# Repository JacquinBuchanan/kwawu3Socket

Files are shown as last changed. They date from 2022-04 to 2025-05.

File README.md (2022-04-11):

# Kwawu Arm 3.0 - Socket Version

This is a 3D Printable functional device for those with forearm limb differences. It has better functionality and easier to assemble than the Kwawu 2.0 version.

!!!! DO NOT PRINT THESE STL FILES DIRECTLY. !!!!!
Download all the files and use the OpenSCAD to modify and scale the STL files.

The included PDF file "Kwawu 3.0 Socket Version Instructional Guide" will show you how to download the Open SCAD program and use the code in these files to size this model.

Instructional videos for this design can be found here.
https://www.youtube.com/playlist?list=PLO2iVws0boe0Yrh_1auXd5TTmXr6_y3zT

I have redesigned the Kwawu arm to be more natural looking and more functional. The terminal device has a much higher grip strength and functionality. Very good at picking up small things with index finger and thumb and big things with whole hand.

This version is the socket version intended for people with short forearm residual limbs.
There is a wrap version for people with long forearm residuals

I would like to thank the e-NABLE community. It is a wonderful group to be a part of.

To get involved with the e-NABLE community please visit https://hub.e-nable.org

Shield: [][cc-by]

This work is licensed under a
[Creative Commons Attribution 4.0 International License][cc-by].

[][cc-by]

[cc-by]: http://creativecommons.org/licenses/by/4.0/
[cc-by-image]: https://i.creativecommons.org/l/by/4.0/88x31.png
[cc-by-shield]: https://img.shields.io/badge/License-CC%20BY%204.0-lightgrey.svg

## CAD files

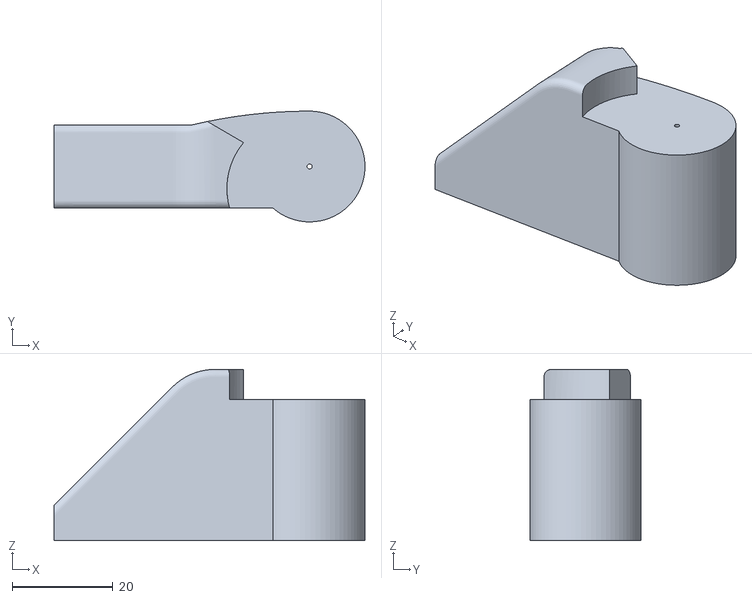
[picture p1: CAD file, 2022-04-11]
o_Arm2.stl
61.7 x 22.0 x 34.0

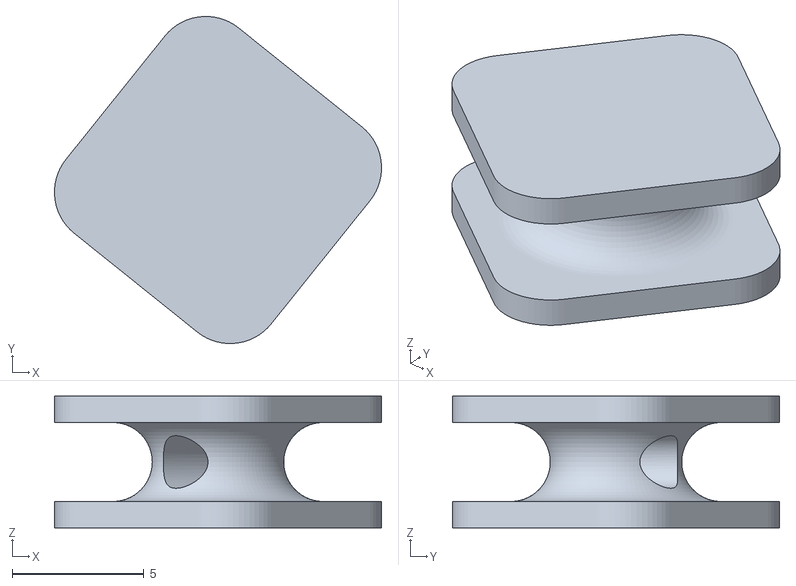
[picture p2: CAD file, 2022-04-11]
o_Tensioner.stl
12.4 x 12.4 x 5.00

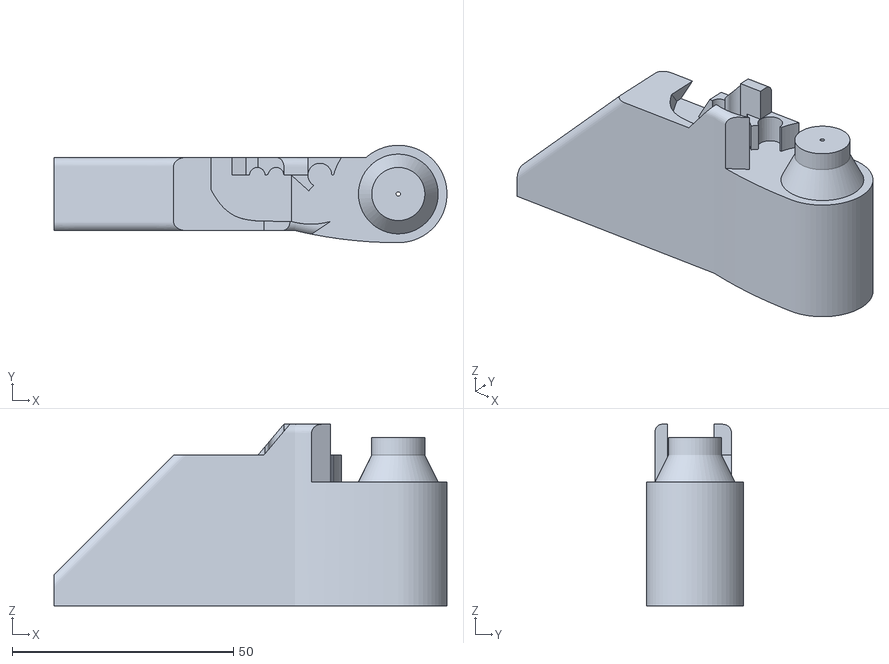
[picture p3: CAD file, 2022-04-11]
o_Arm1.stl
88.7 x 22.0 x 41.0

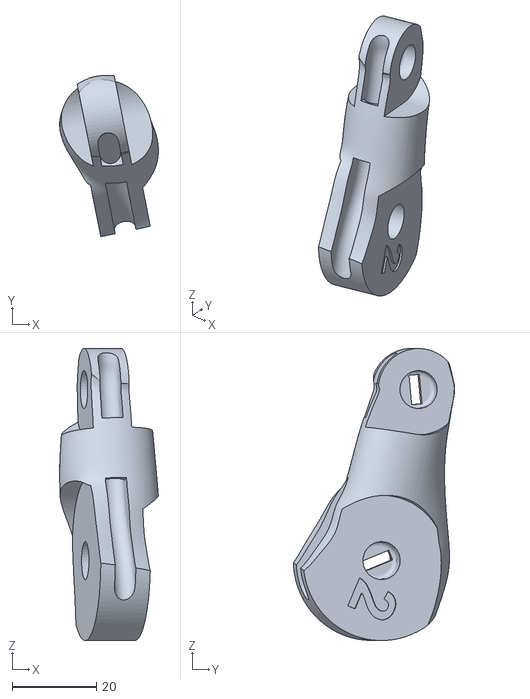
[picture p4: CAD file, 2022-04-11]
o_IndexFingerPhalanx.stl
23.4 x 38.3 x 69.3

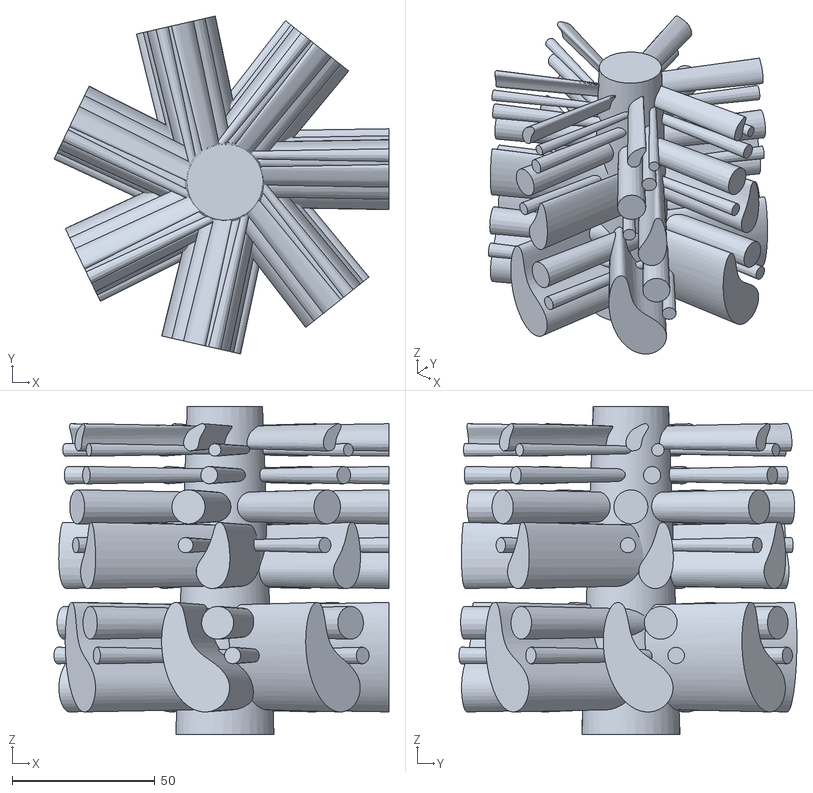
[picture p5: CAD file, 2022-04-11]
o_VentHoles11.stl
117.4 x 118.4 x 115.0

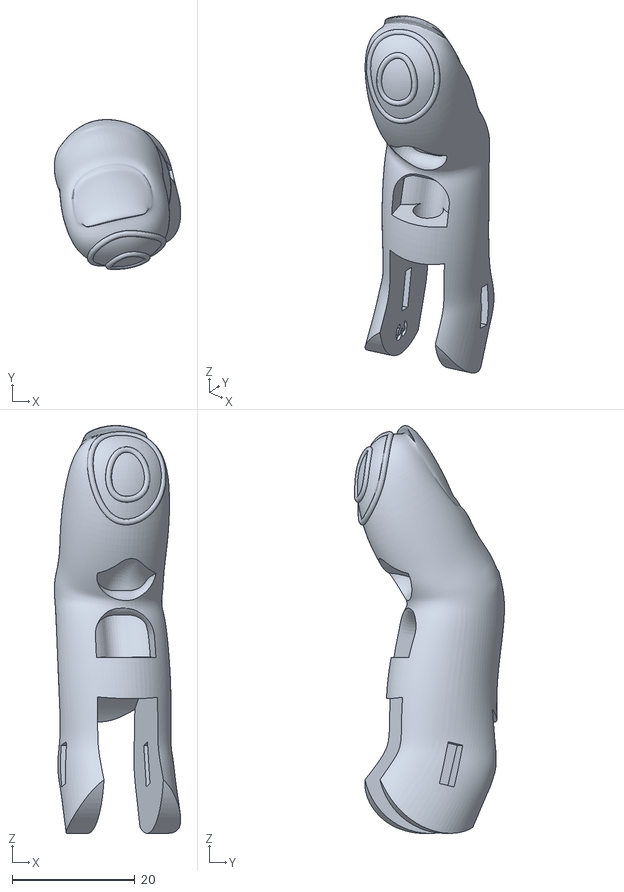
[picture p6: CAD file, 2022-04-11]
o_MiddleFingerEnd.stl
20.6 x 24.5 x 66.6

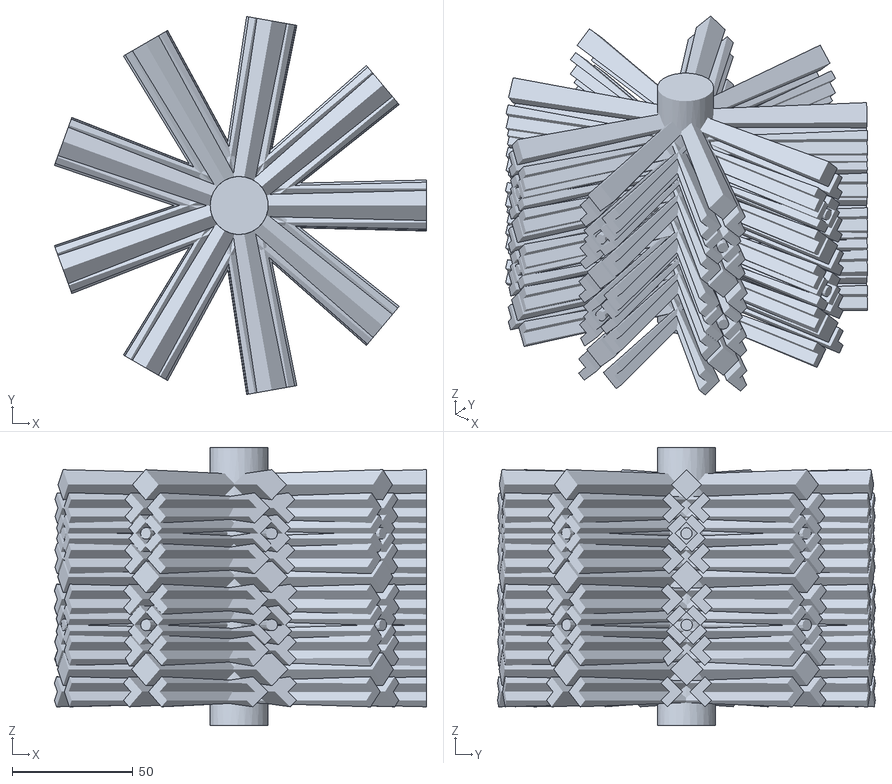
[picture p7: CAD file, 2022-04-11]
o_VentHoles31.stl
153.9 x 156.3 x 115.0

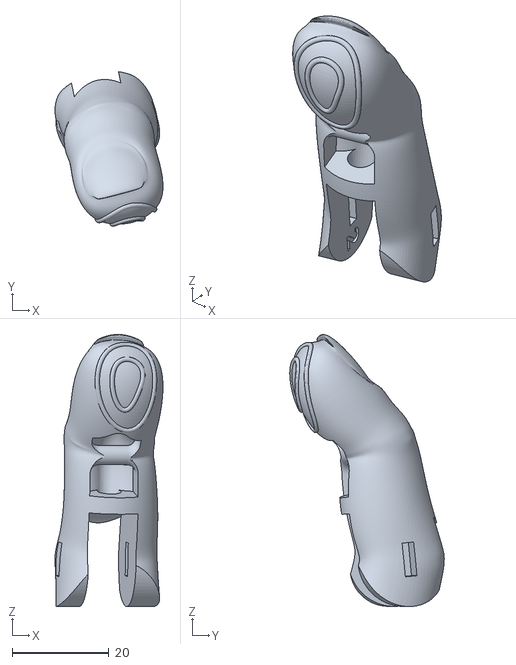
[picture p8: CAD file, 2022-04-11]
o_IndexFingerEnd.stl
22.3 x 31.9 x 56.2

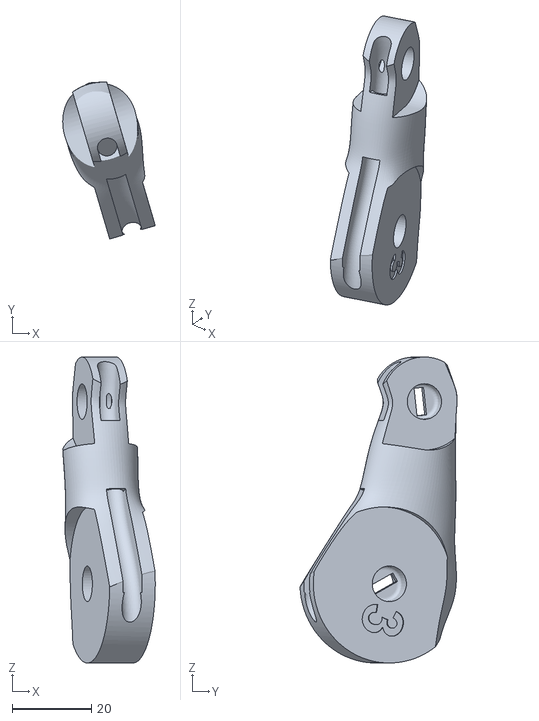
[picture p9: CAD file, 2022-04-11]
o_MiddleFingerPhalanx.stl
23.4 x 39.6 x 77.3

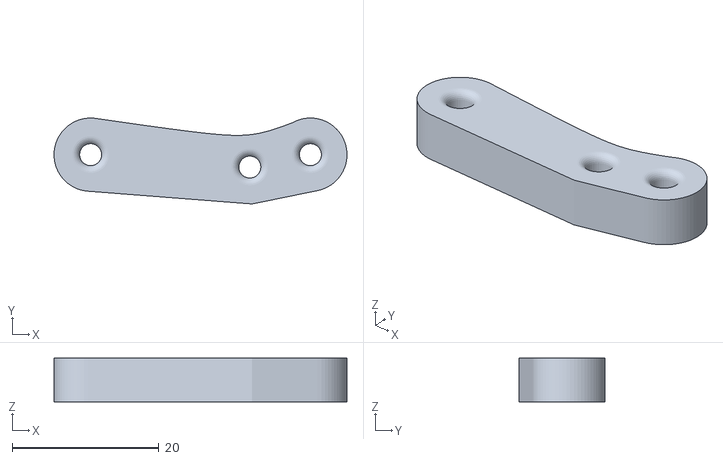
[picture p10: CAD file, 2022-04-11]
o_WhippleTreeSecondary.stl
40.0 x 11.7 x 6.00

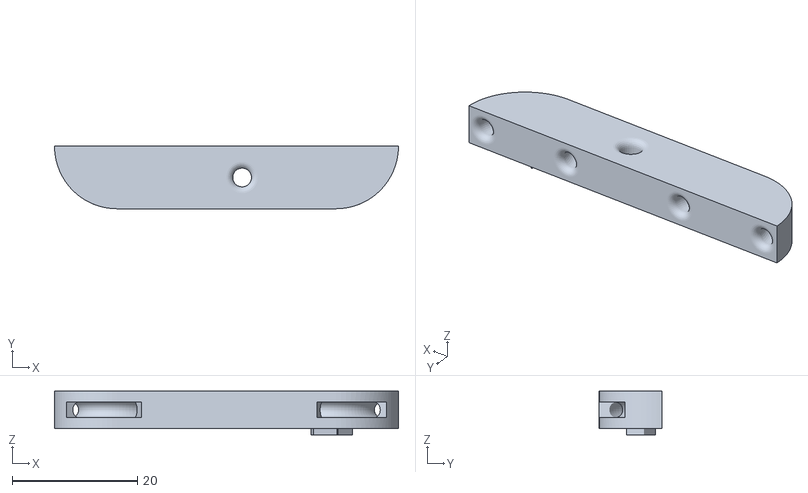
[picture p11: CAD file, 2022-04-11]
o_WhippleTreePrimary.stl
55.0 x 10.0 x 7.00

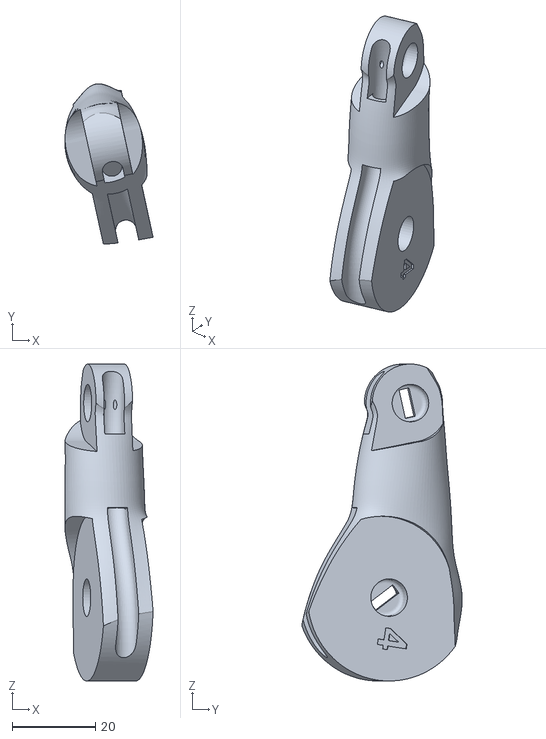
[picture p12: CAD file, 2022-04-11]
o_RingFingerPhalanx.stl
21.1 x 38.5 x 76.1

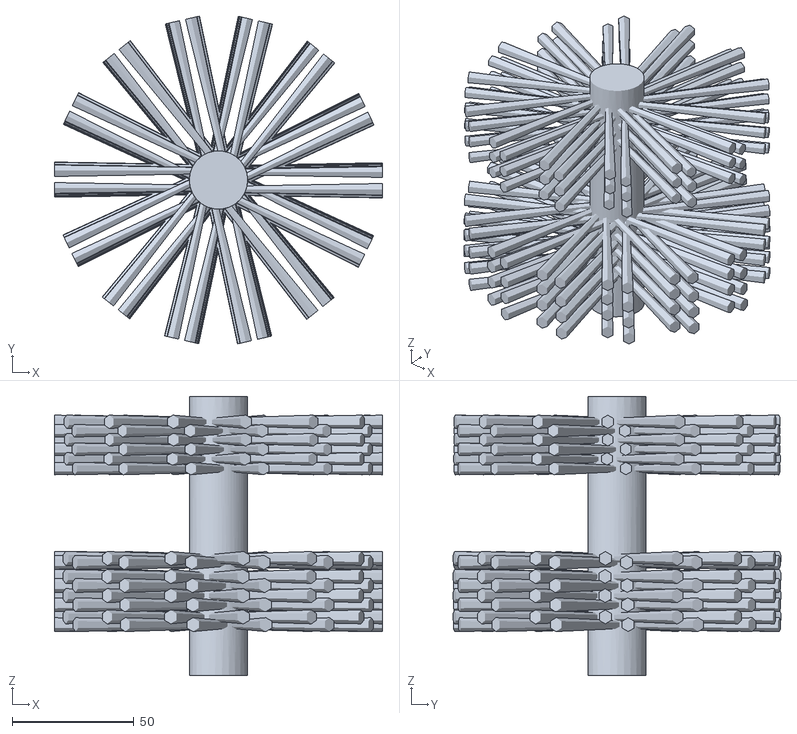
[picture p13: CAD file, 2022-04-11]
o_VentHoles21.stl
135.0 x 134.9 x 115.0

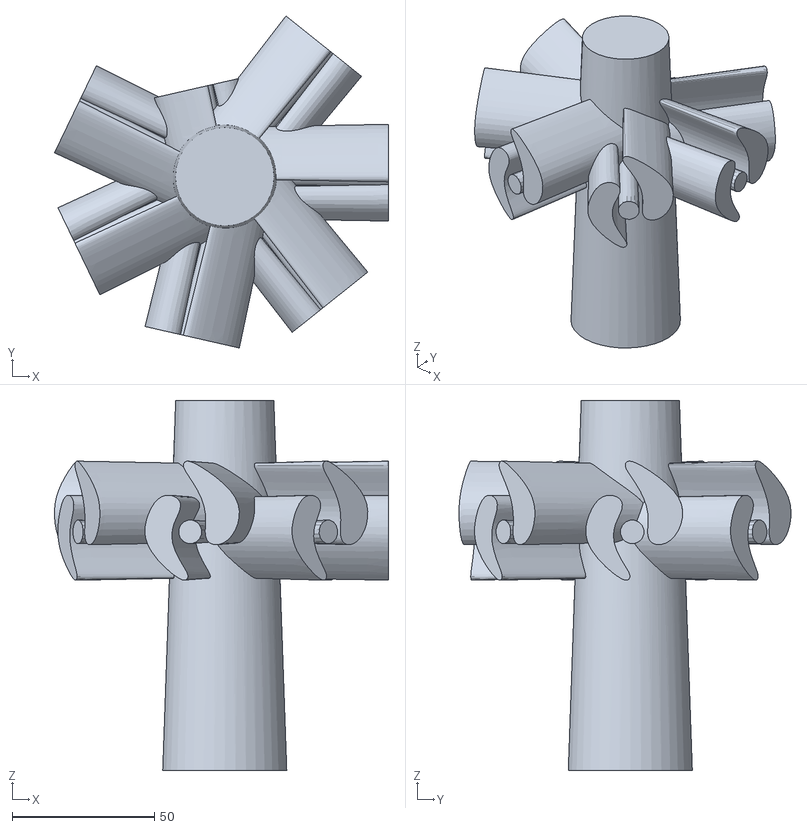
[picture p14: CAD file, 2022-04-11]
o_VentHoles12.stl
117.3 x 116.5 x 130.0

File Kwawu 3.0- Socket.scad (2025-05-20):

// The Kwawu 3.0 prosthetic Arm - Socket Version
// By Jacqun Buchanan
// Parameteric 3-d printable prosthetic arm
//
// This design is licensed under the Creative Commons - Attribution - Share Alike license.

// The ISO thread code is by Trevor Moseley

// The Interpolation and path smoothing code is by Timothy Weber
// https://github.com/teejaydub/tjw-scad

// Choose Part
Part = "Cuff1"; // [Palm,PalmTop,WristButton,WristCover, Cuff1,Cuff2,Cuff3,CuffLeatherTemplate,UpperArm,LowerArm, Ratchet, Latch, LatchCover, WristBolt, WristBoltPinCover, PalmBolt,  ElbowBolt1,ElbowBolt2,IndexFingerEnd, IndexFingerPhalanx, MiddleFingerEnd, MiddleFingerPhalanx, PinkyFingerEnd, PinkyFingerPhalanx, RingFingerEnd, RingFingerPhalanx, ThumbEnd, ThumbPhalanx, Tensioner, WhippleTreePrimary, WhippleTreeSecondary,PencilHolderCover, Hinges]
//Left or Right Arm
LeftRight = "Right"; //[Right, Left]
//Wraps are made from leather or plastic
LeatherOrPlastic = "Leather"; //[Leather, Plastic]
// Across all four knuckles (mm)
HandWidth = 96; //[65:186]
// Elbow crease to wrist attachment (mm)
ArmLength = 271; //[141: 564]
// At what length to split between Upper and Lower arm pieces. Measured from elbow (mm)
ArmSplitLength = 135; //[10: 564]
// Circumferences(mm) of Forearm start at elbow creses seperate by 25mm
ForearmCircumferences1 = [272,268,265,261]; //[0:1:600]
ForearmCircumferences2 = [255,0,0,0]; //[0:1:600]
ForearmCircumferences3 = [0,0,0,0]; //[0:1:600]
// Circumference of Bicep (mm)
BicepCircumference = 294; //[160: 600]
// Padding Thickness -inside forearm and cuff (mm)
PaddingThickness = 2; //[0: 10]
// ISO metric bolt holding palm together (mm) 
PalmBoltDiameter = 6;//[4, 6, 8]
// ISO metric bolt holding cuff and arm together (mm)
ElbowBoltDiameter = 8; //[4, 6, 8, 10, 12, 14]
// Diameter of leather rivet shaft (mm)
RivetShaftDiameter = 5; //[2.4, 2.8, 3.1, 4, 5, 6]
// Velcro strap width (mm)
StrapWidth = 25;//[10: 60]
// Include Pencil Holder
PencilHolder = "No"; // [Yes,No]
// Add Air Venting Holes In Upper Forearm
UpperVentingHoles = "None"; // [None,VentingHoles1,VentingHoles2,VentingHoles3]
// Add Air Venting Holes In Lower Forearm
LowerVentingHoles = "None"; // [None,VentingHoles1,VentingHoles2,VentingHoles3]
// Options for Mechanisim at Elbow
ElbowMechanisims = "Latch and Lever"; // [Latch and Lever,Lever Only,No Lever]  

/* [Hidden] */
ForearmCircumferences = concat(ForearmCircumferences1,ForearmCircumferences2,ForearmCircumferences3);


SlotSize = 0.5;
SlotLength = 10;//length of the opening slot
SlotSpacing = 3;//spacing between slots
SlotWidth = 2.4;//width of slots 
//The thickness of the cuff
ShellThickness = 2;

//The thickness of the Arm
ArmShellThickness = 3;

// This is an amount added to the pencil cover length. 
// When this is zero the pencil cover is as tight as possible.
// Make it larger to fit around larger/thicker pencils
PencilCoverAddedLength = 4.0;

PI =  3.141592653589793238;
HandVersion = "V3.0";

HandScale = HandWidth / 96;
ForearmCircumferenceWPadding = ((ForearmCircumferences[0]/PI) + 2*PaddingThickness)*PI;
ForeArmCircumferenceScale = ForearmCircumferenceWPadding/291;
ElbowPartsScale = max(0.73, ForeArmCircumferenceScale);
ForearmDiameterWPadding = ForearmCircumferenceWPadding/PI;
BicepCircumferenceWPadding = ((BicepCircumference/PI) + 2*PaddingThickness)*PI;
BicepDiameterWPadding = BicepCircumferenceWPadding/PI;
CuffScale = BicepCircumferenceWPadding/270;
CuffLength = CuffScale * 90;
ArmLengthScale = ArmLength/271;


WristBoltDia = 18;
$fn=30;

if(Part == "Cuff1") {
    if (LeftRight == "Left") {
        mirror([1,0,0]) MakeCuff1();
    }else {
        MakeCuff1();
    }
}

if(Part == "Cuff2") {
    if (LeftRight == "Left") {
        mirror([1,0,0]) MakeCuff2();
    } else {
        MakeCuff2();
    }
}

if(Part == "Cuff3") {
    if (LeftRight == "Left") {
        mirror([1,0,0]) MakeCuff3();
    } else {
        MakeCuff3();
    }
}

if(Part== "CuffLeatherTemplate")
    {
    if (LeftRight == "Left") {
        mirror([1,0,0]) MakeCuffLeatherTemplate();
    } else {
        MakeCuffLeatherTemplate();
    }
}

if(Part == "UpperArm") {
    if (LeftRight == "Left") {
        mirror([1,0,0]) MakeArmUpper();
    } else {
         MakeArmUpper();
    }
}

if(Part == "LowerArm") {
    if (LeftRight == "Left") {
        mirror([1,0,0]) MakeArmLower();
    } else {
        MakeArmLower();
    }
}


if(Part == "Ratchet") {
    if (LeftRight == "Left") {
        mirror([1,0,0]) MakeRatchet();
    } else {
        MakeRatchet();
    }
}

if(Part == "Tensioner")
    MakeTensioner();

if(Part == "Latch") {
    if (LeftRight == "Left") {
        mirror([1,0,0]) MakeLatch();
    } else {
        MakeLatch();
    }
}

if(Part == "LatchCover") {
    if (LeftRight == "Left") {
        mirror([1,0,0])  MakeLatchCover();
    } else {
        MakeLatchCover();
    }
}


if(Part == "WristBolt") {
    if (LeftRight == "Left") {
        mirror([1,0,0]) rotate(a=[180,0,0])MakeWristBolt();
    } else {
        rotate(a=[180,0,0])MakeWristBolt();
    }
}

if(Part == "WristBoltPinCover")
{
    if (LeftRight == "Left") {
        mirror([1,0,0]) MakeWristBoltPinCover();
    } else {
        MakeWristBoltPinCover();
    }
}

if(Part == "ElbowBolt1"){
    if (LeftRight == "Left") {
        mirror([1,0,0]) rotate(a=[180,0,0]) MakeElbowBolt(16);
    } else {
        rotate(a=[180,0,0]) MakeElbowBolt(16);
    }
}

if(Part == "ElbowBolt2"){
    if (LeftRight == "Left") {
        mirror([1,0,0]) rotate(a=[180,0,0]) MakeElbowBolt(9);
    } else {
        rotate(a=[180,0,0]) MakeElbowBolt(9);
    }
}

if(Part == "PalmBolt"){
    if (LeftRight == "Left") {
        mirror([1,0,0]) rotate(a=[180,0,0])MakePalmBolt();
    } else {
        rotate(a=[180,0,0])MakePalmBolt();
    }
}

if (Part == "Palm") {
    if (LeftRight == "Left") {
        mirror([1,0,0]) MakePalm();
    } else {
        MakePalm();
    }
}

if(Part =="WristButton")
{
    //Rotate just to orient for printing
    if (LeftRight == "Left") {
        mirror([1,0,0]) rotate(a=[180,0,0])MakeWristButton();
    } else {
    
        rotate(a=[180,0,0])MakeWristButton();
    }
}

if(Part =="WristCover")
{
    MakeWristCover();
    
}

if (Part == "PalmTop") {
    //Rotate just to orient for printing
    if (LeftRight == "Left") {
        mirror([1,0,0]) rotate(a=[90,7,]) MakePalmTop();
    } else {
        rotate(a=[90,7,0])MakePalmTop();
    }
}

if(Part == "IndexFingerEnd") {  
    if (LeftRight == "Left") {
        mirror([1,0,0]) IndexFingerEnd();
       } else {
        IndexFingerEnd();
    }
}

if(Part == "IndexFingerPhalanx") { 
     if (LeftRight == "Left") {
        mirror([1,0,0]) IndexFingerPhalanx();
       } else {
        IndexFingerPhalanx();
    }
}
        
if(Part == "MiddleFingerEnd") { 
     if (LeftRight == "Left") {
        mirror([1,0,0]) MiddleFingerEnd();
       } else {
        MiddleFingerEnd();
    }
}
            
if(Part == "MiddleFingerPhalanx") { 
     if (LeftRight == "Left") {
        mirror([1,0,0]) MiddleFingerPhalanx();
       } else {
        MiddleFingerPhalanx();
    }
}
                
if(Part == "PinkyFingerEnd") { 
     if (LeftRight == "Left") {
        mirror([1,0,0]) PinkyFingerEnd();
       } else {
        PinkyFingerEnd();
    }
}

if(Part == "PinkyFingerPhalanx") { 
     if (LeftRight == "Left") {
        mirror([1,0,0]) PinkyFingerPhalanx();
       } else {
        PinkyFingerPhalanx();
    }
}

if(Part == "RingFingerEnd") { 
     if (LeftRight == "Left") {
        mirror([1,0,0]) RingFingerEnd();
       } else {
        RingFingerEnd();
    }
}

if(Part == "RingFingerPhalanx") { 
     if (LeftRight == "Left") {
        mirror([1,0,0]) RingFingerPhalanx();
       } else {
        RingFingerPhalanx();
    }
}

if(Part == "ThumbEnd") { 
     if (LeftRight == "Left") {
        mirror([1,0,0]) ThumbEnd();
       } else {
        ThumbEnd();
    }
}

if(Part == "ThumbPhalanx") { 
     if (LeftRight == "Left") {
        mirror([1,0,0]) ThumbPhalanx();
       } else {
        ThumbPhalanx();
    }
}

if(Part == "WhippleTreePrimary") { 
     if (LeftRight == "Left") {
        mirror([1,0,0]) rotate(a=[180,0,0])WhippleTreePrimary();
       } else {
        rotate(a=[180,0,0])WhippleTreePrimary();
    }
}

if(Part == "WhippleTreeSecondary") { 
     if (LeftRight == "Left") {
        mirror([1,0,0]) WhippleTreeSecondary();
       } else {
        WhippleTreeSecondary();
    }
}

if(Part == "PencilHolderCover")
{
    PencilHolderCover();
}
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

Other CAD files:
o_PencilHolderTool.stl
o_Ratchet.stl
o_PinkyFingerPhalanx.stl
o_Cuff1.stl
o_Cuff2.stl
o_Latch.stl
o_LatchCover.stl
o_Palm.stl
o_PalmTop.stl
o_PinkyFingerEnd.stl
o_RingFingerEnd.stl
o_ThumbEnd.stl
o_ThumbPhalanx.stl
o_VentHoles22.stl
o_VentHoles32.stl

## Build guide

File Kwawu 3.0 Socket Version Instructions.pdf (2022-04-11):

# Kwawu Arm 3.0

# Socket Version

# Instruction Guide

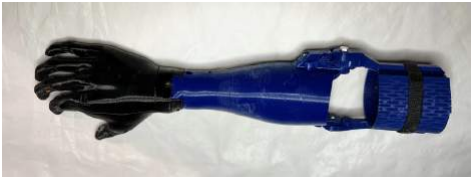
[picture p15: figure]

# Jacquin Buchanan January 2022

This work is licensed under the Creative Commons Attribution 4.0 International License. To view a copy of this license, visit https://creativecommons.org/licenses/by/4.0/ or send a letter to Creative Commons, PO Box 1866, Mountain View, CA 94042, USA.

In simple language you can:
- Share — copy and redistribute the material in any medium or format.
- Adapt — remix, transform, and build upon the material for any purpose, even commercially.
Under the following terms:
- Attribution — You must give appropriate credit, provide a link to the license, and indicate if changes were made. You may do so in any reasonable manner, but not in any way that suggests the licensor endorses you or your use.
- No additional restrictions — You may not apply legal terms or technological measures that legally restrict others from doing anything the license permits.

Kwawu Arm 3.0 Socket Version 2

This instruction guide shows the steps and processes in making a Kwawu 3.0 Socket Version transradial prosthetic arm and hand. This socket prosthetic arm is best suited for a recipient with a residual forearm that is half or shorter in length compared to the recipient’s intact forearmarm. See the Wrap version of the Kwawu 3.0 for an arm better suited for recipients with a residual arm longer than half the intact arm.

Improvements of the Kwawu 3.0 over the Kwawu 2.0 device include:

- Easier stringing the fingers to hand mechanism
- Better response of elbow bend to finger squeeze
- A locking but adjustable wrist
- Improved latch mechanism to fix hand fingers in a grasped position
- The Cuff has a plastic and leather option
- Thermoforming is not required
- A redesigned tensioner
- Easier assembly
- Compatible with wider range of TPU ShoreA hardnesses

# Qualifying Expectations

This arm was designed by hobbyists in hopes that it would fill a need for someone who has had a congenital or traumatic amputation. We do not claim to be professional prosthetists and this arm is designed as an assistive device not a custom prosthetic. This was designed to be used as an assist in everyday functional activities. These are step by step instructions for fabrication of the arm. Our team is available to help problem solve and answer questions should you have difficulties. If you are in need of this assistive device but are unable to make it or have it made we are happy to assist with that as well. As hobbyists our goal is to help make an assistive device which makes day to day activities a little easier.

To complete the instructions in this document and fully prepare an arm for usage can take 30 to 40 hours of labor. Assuming most people reading this document are doing this project in their spare time, expect it to take several weeks. Likely the first one you make may not fit or work exactly right, when you try it on the recipient, so you will have to reprint a part and partially reassemble the arm. It is important to set this expectation for yourself and the person you are making the arm for. Explain to them and yourself that the whole process can take months.

## This Process of making a Kwawu 3.0 Socket Arm is described in the document and is divided into 3 sections, namely:

### Section 1: Preparing Files for Printing

## Section 2: 3D Printing of the Necessary Parts

## Section 3: Assembly of the Kwawu Arm 3.0 Socket Version

# Section 1: Preparing Files for Printing

## Overview

1. Download the Kwawu 3.0 Socket version from www.thingiverse.com. (http://www.thingivers.com) DO NOT print the stl files directly—they will not result in a functional device—files must be translated into usable stl files using the customizer in OpenSCAD.
2. Download the latest version of OpenSCAD from http://openscad.org/downloads.html Then open the file “Kwawu 3.0- Socket.scad.
3. Obtain required measurements from the recipient — Record values for the recipient in Table 1.
4. Fill in the OpenSCAD parameters with the specific values of the recipient’s measurements.
5. Render all appropriate parts in the display and save the result as a file.

## Download Kwawu 3.0 files

When you download the files from thingiverse there is one .scad file and a bunch of .STL files. DO NOT print the STL files directly. The Open SCAD software will load the STLs and “modify “ them to fit the recipient.

## Download and Install OpenSCAD

1. Download and install the latest version of OpenSCAD. http://openscad.org/downloads.html
2. Once you have installed OpenSCAD, click on “New” then in the top menu, select File>Open. Browse and click on the file “Kwawu 3.0 Socket.scad”
3. Uncheck ‘Hide Customizer” in the View menu (as shown below) to show the Customizer UI at the right.

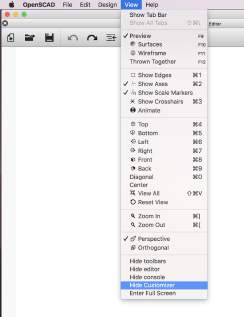
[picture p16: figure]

4. In the Customizer menu on the Right Hand side, click the little black arrow to display the parameters. Make sure “Automatic Preview” and “Show Details” are both checked.

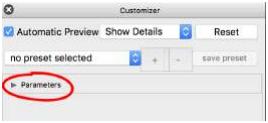
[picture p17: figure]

5. Hit the Preview button (F5) to get a quick preview (should not be necessary if ‘Automatic preview’ is enabled).
6. You should see a preview of the Cuff1 in the main window. It looks something like this.

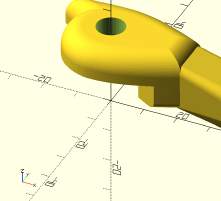
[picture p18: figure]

7. If the object is too large or small press the “View all” button

The view will change to something like this.

Now you are ready to set all the sizing parameters. Once you have set all the parameters you will need to render each part and save to file.

## Measuring Your Recipient

There are several measurements you will need from the recipient. The circumference measurements you will want to make on the residual arm. The Forearm Length and Hand Width you will make on the intact arm. All measurements are in millimeters.

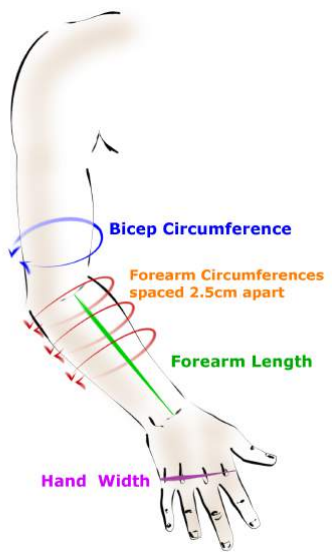
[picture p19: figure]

Measurements Diagram

Bicep Circumference: Measured around the upper arm at its thickest point. Measured on the residual arm being fitted with the prosthesis.

Forearm Circumferences: This is a series of measurements meant to capture the shape of the forearm socket. Starting at the recipient’s elbow crease, measure the arm’s circumference and every subsequent 25mm, until you reach the end. Measured on the residual arm being fitted with the prosthesis.

Forearm Length : Measured from the elbow crease to the wrist crease on the recipient’s intact arm. We recommend you use a measurement at least 5% to 10% shorter than the intact arm to improve maneuverability and better mechanical advantage of the prosthetic arm. If the recipient does not mind, you can make the arm length only slightly longer than the residual arm, (leaving enough space for the wrist mechanism)--this will have a less natural look but may be more functional. It is a preference to discuss with the recipient.

Hand Width: Measured on the intact arm. The measurement is across the knuckles in millimeters.

## Fill in the OpenSCAD parameters

Once you have measurements from the recipient you will enter various parameters into the Customizer Parameters side bar.

The below example is a screen capture of the OpenSCAD customizer for the socket version. The measurements from the recipient need to be inputted in the appropriate parameters as well as other choices that need to be decided upon consulting the recipient. All these inputs will be discussed separately.

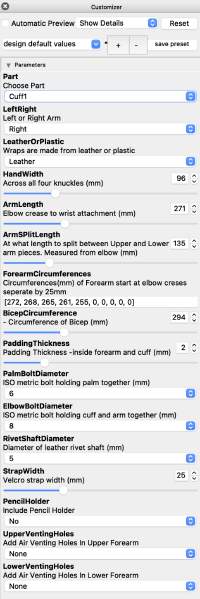
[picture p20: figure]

In OpenSCAD, It may be easier to turn OFF Automatic Preview while entering parameters. Many of these parts are slow to render so having the preview run while entering numbers can make the user interface cumbersome.

Detailed information on choices is necessary to render parts to make printable stl files. All 3D parts to be printed must be rendered using the selected choices matching the recipient’s measurements and/or preferences. A description of these choices are listed below in order. Table 1 shows the acceptable ranges of these choices and allows you to fill in specific values for your recipient

OpenSCAD Parameters

Parameter Name | Description
Part | This is a list of all the parts necessary to assemble a Kwawu3 Socket Arm. Choose each of the 33 parts, one by one, then render and save each one. Before rendering any parts, be sure all the other parameters are set to match the recipient. Input or use the sliders to set the values. Uncheck “Automatic Preview'' if you have issues with inputting values. After rendering, go to File>Export>As STL . Name the file to correspond to the part rendered and Save. See “Leather or Plastic'' for an exception in the export file choice.
Left or Right Arm | The side of the body for the prosthetic arm required by the recipient.
LeatherOrPlastic | The leather option is for the cuff (bicep) area of the device for the socket version. Leather may be a more comfortable option over the plastic version. If the Leather option is chosen, the part “Cuff Leather Template” must be rendered and the result exported: go to File>Export>Export as SVG. Name the file compatible with the template such as “CuffLeatherTemplate “ and save. Note that Cuff3 will not render if the Leather Option is chosen.
Handwidth | Measure the width of the recipient’s intact hand at the knuckles.
ArmLength | Arm length is typically chosen based on the recipient’s “good” arm—or it may be purposely made shorter for easier maneuverability and better mechanical advantage. The socket version is primarily meant for recipients with a residual arm less than half as long as the recipient’s intact arm.
ArmSplitLength | If the arm length chosen is too long for your printer, the forearm can be printed in two parts—the UpperArm and LowerArm. If two parts are required, make sure you choose the split point longer than the recipient’s residual, and not too close to the wrist (i.e. Do not let the arm split interfere with the wrist bolt). If you choose to make the forearm in one print, set the ArmSplitLength longer than the ArmLength—there is then no need to render LowerArm.

Forearm Circumferences | Insert in the parentheses a series of forearm circumference measurements (comma separated) starting at the recipient’s elbow crease and every subsequent 25mm. Once past the recipient's residual length, leave 0’s as the remaining numbers. Generally the circumferences should always be decreasing in value, though this is not required. If a circumference step increases, be sure the recipient can still fit their arm in the socket past the tight spot.
Bicep Circumference | Measure the circumference of the bicep where the cuff will wrap around.
Padding Thickness | Padding is inserted in the upper arm area where the recipient’s forearm residual will contact the prosthetic. The more comfortable option is silicone sheeting —e.g.

https://amputeestore.com/products/silipos-pressure-relief-gel-padding?variant=4 114763009 (https://amputeestore.com/products/silipos-pressure-relief-gel-padding?variant=4114763009) — but the more expensive option.

Closed cell neoprene is a less expensive but still a good option. Here are links to a couple of these:
https://www.amazon.com/Insulation-Neoprene-Adhesive-Multi-Function-Soundproof/dp/B08R9LF7BX (https://www.amazon.com/Insulation-Neoprene-Adhesive-Multi-Function-Soundproof/dp/B08R9LF7BX)

https://www.amazon.com/NATGAI-Neoprene-Adhesive-Multiple-Dimensions/dp/B07VY7SFRP (https://www.amazon.com/NATGAI-Neoprene-Adhesive-Multiple-Dimensions/dp/B07VY7SFRP)
2mm is the typical thickness for padding.
PalmBolt Diameter | Bolts for the palm can be printed, however, we recommend small bolt sizes (diameter 4mm or less) should be purchased as metal or nylon bolts to reduce the chance of bolt breakage. Also, we recommend the sizes chosen to be in proportion to the arm size, i.e. use small bolts for a small arm and a larger one for larger arms.
ElbowBolt Diameter | Bolts for the elbow can also be printed, however, we recommend small bolt sizes (diameter 4mm or less) should be purchased as metal or nylon bolts to reduce the chance of bolt breakage. Also we recommend the sizes chosen to be in proportion to the arm size, i.e. use small bolts for a small arm and larger one for larger arms.
RivetShaft Diameter | Rivet shaft diameter only applies to the leather version and to how large the holes should be in Cuff 1 and Cuff 2 parts. Rivet shafts come in different sizes. An alternative to rivets are Chicago screw/post sets.
StrapWidth | Velcro Straps are required on the Cuffs for both the leather and plastic versions. Strap widths of 25 mm are typically used for larger sized arms and 10mm for small sizes.

PencilHolder | A Pencil holder on the palm is an option and should be made with TPU.

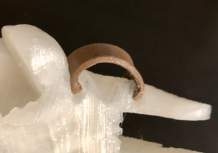
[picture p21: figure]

UpperVentHoles | Vent holes in Arm1 (UpperVentHoles) are an option for the Kwawu 3 socket version. Different designs or no vent holes are shown so you can choose the pattern (or no venting) as desired. Vent holes are recommended in the area below the arm residual.
LowerVentHoles | Vent holes in the Arm2 (LowerVentHoles) are also an option for the Kwawu 3 socket version. See description in UpperVent Holes.

Table 1 shows a list of choices that must be made in the OpenSCAD customizer along with ranges and units of each. The column on the right allows the maker to record the choices used for a specific recipient. Many of the choices require measurement on the recipients.

Table 1: OpenSCAD Options and Ranges

| Parameter Range | units | Recipient Values
Part | See separate list | | n/a
Left or Right | Left or right
Leather or Plastic | Leather or Plastic
Handwidth | 65 - 186 | mm
ArmLength | 141-564 | mm
ArmSplitLength | 10-564 | mm
ForearmCircumference | see prior description | mm
BicepCircumference | 160-600 | mm
PaddingThickness | 0-10 | mm

PalmBoltDiameter | 4, 6, or 8 | mm
ElbowBoltDiameter | 4, 6, 8, 10, 12 or 14 | mm
RivetShaftDiameter | 2.4, 2.8, 3.1, 4, 5, or 6 | mm
StrapWidth | 10-60 | mm
PencilHolder | yes or no
UpperVentHoles | 0, option 1, 2, or 3
LowerVentHoles | 0, option 1, 2, or 3

## Render all appropriate parts

Select each part in the Parts dropdown.Then Press Render.

NOTE: The render button can take a long time for some parts (20 minutes or more).

Save STL (exception—leather template). Export and save the stl files under a name that identifies each part. For the CuffLeatherTemplate choose FILE->EXPORT->EXPORT As SVG

# Section 2: 3D Printing of Necessary Parts

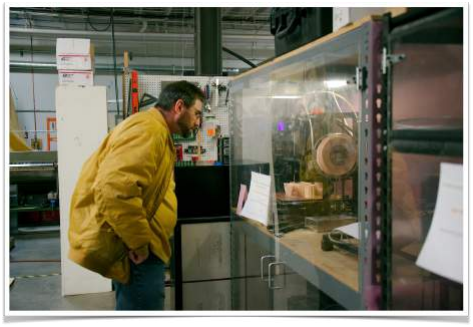
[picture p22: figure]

Table 2 shows all parts available for printing along with quantity required, material typically used, and if supports (bed contact) are generally used. PETG is the material recommended for most of the parts because of its strength and solvent resistance—other materials may be tried but we cannot predict a good outcome. Use a suitable TPU for hinges and the pencil holder.

Printing Recommendations

Typical print temperature and print speed recommended for the material (PETG or TPU).

Infil should be 35% and of honeycomb geometry.

If you are using a printer with a 0.5mm nozzle, you may find a linewidth of 0.4mm works better for some parts (e.g. latch).

We recommend the number of top and bottom layers to be 10 layers. The reason is that the 2mm flexible plastic grid in the case of the plastic cuff has been engineered for flexibility and strength as a solid device. If 10 layers for both and bottom layers are used, we can be certain the grid will be solid but changes won’t be necessary for other parts. Make sure the gaps in the grid are open—if not you may need to raise the z height so the bottom layer/layers will not be spread out which could cause gaps to be fused closed. If gaps are closed, the grid may be inflexible.

### Note: All the parts are rendered from OpenSCAD in the orientation we think is best for printing. Though, you may need to adjust the orientation based on

your particular printer.

A brim is recommended for the finger ends and phalanxes to enhance part stability during printing.

Printing the finger pieces can also benefit from
supports/scaffolding. Generally it is better to use a slicing
program that will let you manually place the scaffolding
for these parts. If you are having trouble with the fingers coming loose from the base plate, try learning them back to a 45 degree angle and adding more scaffolding. This may add to the time to clean the parts, but can be more reliable for some printers.

### Note: If scaffolding is used, it is better to be manually added than be auto-generated by the printing software. Auto-generated scaffolding can

block holes and make it very difficult to string the hand.

### Make sure to review the scaffolding so it DOES NOT get created inside a

channel or hole where it can be very difficult to remove.

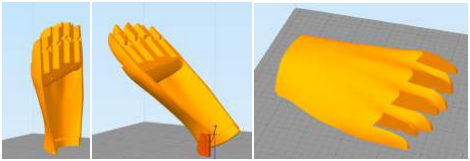
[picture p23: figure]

Three orientations to print the Palm Top. The 45 degree angle was suggested by Krzysztof Grandys and is my preferred orientation for best look and strength.

If leather was chosen for the cuff, open the SVG file (saved in the OpenSCAD procedure) in your browser. We have found the Chrome Browser opens with an accurate size representation so that you can simply print out the template on paper . We have also used Safari to open the SVG file but found it necessary to size the printing to march the holes in the cuffs. Once an accurate template is printed, lay it out on the leather and cut the outline. Plan to use the smoothest side of the leather in contact with the recipient’s skin for greater comfort. A leather punch is recommended to make accurate holes in the leather where it will attach to the Cuff1 and Cuff2 plastic. We also recommend ~4.5 oz leather (~1.8mm thick). It is the more expensive option but we believe it to be more comfortable than the plastic. A website of one supplier of cowhide leather is
www.montanaleather.com

One choice that is not required in the OpenSCAD options is arm color. The recipient should be consulted about their choice in color for their arm so the printer can purchase a filament color as close as possible to the recipient’s choice. If a suitable color is not found, it is possible to use spray paint to better match the recipient’s choice. The arm may also be decorated according to the recipient’s wishes.

Total printing time for all parts may be 30 to 40 hours. After each print, remove any support structures and sand or file any rough edges or corners. Additional sanding or filing may be necessary when fitting parts together during assembly. Printing several small parts in the same print job will cut down on total print time.

TPU is required for hinges and the pencil holder. Hinges have been design engineered to use a TPU of Shore A hardness range of 85A to 95A . ShoreA hardness 85A is preferred but more difficult to print than 95A. The brand NinjaFlex is the original material from a company called NinjaTek. They have since come out with several other flexible filaments all with different

properties, so be sure to get the one with Shore A Hardness of 85A.

### Likewise, FilaFlex is a company whose original product was Shore Hardness 82A. They have since come out with FilaFlex Medium which is Shore A Hardness 95A. Shore A Hardness 95A will work for Kwawu 3.0 hinges but since it is stiffer than ShoreA Hardness of lesser values, it would be less

responsive.

### For hinges, make sure the printed parts fit into their appropriate slots snuggly, i.e. will not fall out and will fit into the slots without trimming. Since printers can vary, it may be necessary to scale the print in your slicer to

obtain a proper fit.

Table 2: Printing the Parts

Parts | Quantity | Material | Supports | Parts | Quantity | Material | Supports
Palm | 1 | PETG | yes | ElbowBolt2 | 0 or 1 | PETG/ metal/ nylon | no
PalmTop | 1 | PETG | optional | Index FingerEnd | 1 | PETG | optional
WristButton | 1 | PETG | no | Index Finger Phalanx | 1 | PETG | optional
WristCover | 1 | PETG | no | Middle FingerEnd | 1 | PETG | optional
Cuff1 | 1 | PETG | yes | Middle FInger Phalanx | 1 | PETG | optional
Cuff2 | 1 | PETG | yes | Pinky FIngerEnd | 1 | PETG | optional
Cuff3 | 0 or 1 | PETG | no | Pinky Finger Phalanx | 1 | PETG | optional
CuffLeatherTemplat | 0 or 1 | | n/a | RingFingerEnd | 1 | PETG | optional
UpperArm | 1 | PETG | optional | RingFIngerPhalanx | 1 | PETG | optional
LowerArm | 1 | PETG | no | ThumbEnd | 1 | PETG | optional
Ratchet | 1 | PETG | yes | Thumb Phalanx | 1 | PETG | optional
Latch | 1 | PETG | no | Tensioner | 1 | PETG | no
Latch Cover | 1 | PETG | no | Whipple Tree Primary | 1 | PETG | no
WristBolt | 1 | PETG | no | Whipple Tree Secondary | 1 | PETG | no
WristBolt PinCover | 1 | PETG | no | Pencil Holder | 0 or 1 | TPU | no
PalmBolt | 0 or 2 | PETG/ metal/ nylon | no | Hinges | 1 set | TPU | no
ElbowBolt1 | or | PETG / metal/ nylon | no

# Section 3: Kwawu 3 Assembly-Socket Version

## How does the Arm Work?

Familiarize yourself with the function of the arm prior to building. The fingers are supposed to close with the thumb first and the pinky last. When the fingers close in order, you get the precision of the thumb and index finger first, while the remaining fingers are still out of the way. This enables you to pinch or to pick up finer objects. If you continue to close the grip the other fingers engage as would happen around a bottle or baseball.

The wrist button allows the wrist to freely rotate when pressed and “lock” in place when released. Different wrist positions are useful for different applications.

The latch allows the grip to stay closed tight with the elbow moving freely. With the latch open, the grip opens and closes with the elbow movement. With the latch closed, the string is held as the elbow closes. This allows the user to hold a grip while still using the elbow motion. An example where the latch is useful is when the user needs to hold a spoon while eating or a grabber bag while walking. Move the latch slider back to the open position to release the grip.

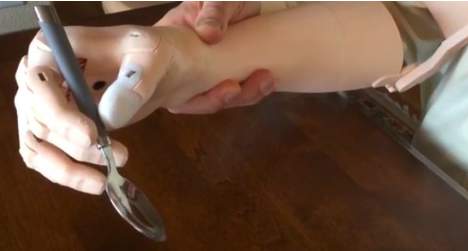
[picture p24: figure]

Note: Assembly videos have been prepared and are supplemental or maybe used in place of this document. See at www.onemonkclapping.com

## Overview

Phase 1 : Preparation
- Gather Materials
- Identify and Arrange Parts
- Prepare the Printed Parts Phase 2 : Hand
- Assembling the Hand
- Stringing the Hand
- Tensioning
Phase 3: Forearm
- Assembling the Forearm
- Assemble the Cuff
Phase 4: Putting it all together
- Attaching Hand to Arm
- Assembling the Latch
- Final Tensioning and Knotting Phase 5: Final Tests and Fitting
- Straps, Finger Tips, and Palm Grip
- Padding and Fitting

## Gather Materials Tools needed for Assembly

We tried to keep the required tools list as short as possible.

Thick CA glue such as Super Glue for sealing the knots in the fishing line and for assembling the forearm.

Two part epoxy is better to assemble arm pieces, if you print the arm in two pieces.

Phillips head screwdriver to fit the Sheet metal screws (#4 pan head)

Hexagonal allen wrench or Robertson square head drive. Depends if you use metal purchased bolts or the 3d printed bolts.

Sharp knife or scissors to cut the fishing line.

## Tools Recommended for Assembly

These tools will make your assembly easier and generally result in a better device.

Small flat file , Small round file , Medium half round file sanding blocks or sandpaper to clean printed parts.

Toothpick or similar disposable fine tip to help spread the glue.

Utility knife or razor to help clean parts. A sharp razor is helpful to clean “stringing” off the flexible parts and is very useful to trim the hinges.

A pair of needle nose pliers can come in handy, particularly when removing scaffolding.

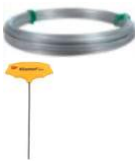
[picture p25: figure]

Galvanized Picture Hanging Wire and/or a T handle Ball End Allen Wrench
Both are very useful in clearing the string holes in the fingers and palm if they close up during 3-D printing. The wire helps pass the string in difficult places. Galvanized wire comes in many sizes at the local hardware store. It is generally stiff enough to force through the holes to open them up.

Plasti Dip - clear
We paint this on the fingertips and the entire palm grip area. This creates a much better grip, then the plastic by itself. It is durable when used with the primer.

A thread Tap tool is handy. You can always heat a metal bolt and use it to clean the threads in the plastic. But a tapping tool is made to do this. You likely will only need a few sizes which correspond to the size of your palm and elbow bolts.

## Parts and Supplies

These are the materials you will use for each build.

Dyneema fishing line—80 to 120 test strength Dyneema is the name of material used in recommended fishing line. For a 100% size hand you will need about 10 feet. Purchase extra to allow for adjustments in tensioning and restringing of the hand. (e.g. brand names include Spiderwire or Hercules).

Steel rod of 2mm diameter.
2mm rods are available on Amazon. https://www.amazon.com/gp/product/B07D2WSF29
Typical wire clothes hangers are suitable or hardware stores sell this diameter steel.
We only need a small piece to stabilize the latch mechanism.

Self Adhesive Padding in areas intended to be in contact with the recipient’s skin (cuff and forearm) is recommended. The thickness of this padding should have already been designated in the OpenSCAD “padding thickness” choice section. If the leather option is chosen for the cuff, no padding is needed in the cuff-but recommended for the socket.
Silicone: https://amputeestore.com/products/silipos-pressure-relief-gel-padding Neoprene:
https://www.amazon.com/Insulation-Neoprene-Adhesive-Multi-Function-Soundproof/dp/B08R9LF7BX
or
Neoprene:
https://www.amazon.com/NATGAI-Neoprene-Adhesive-Multiple-Dimensions/dp/B07VY7SFRP

Velcro Straps —the width of these straps should have been already designated in the OpenSCAD “StrapWidth” choice option. Generally, 8” to 12” long, 1” wide, non-elastic (often sold as cable straps). For small arms you can use 1/2” wide

Palm bolts Cap Head It is recommended to use store bought nylon bolts because they are lighter than metal bolts and more durable than the 3-D printed ones.
The bolts need to match the thread size specified in the OpenSCAD. Most hardware stores will carry these bolts.

Elbow Bolts round head - A nice smooth round head store bought nylon bolt is the best option. When printing with PETG I have had good luck with the printed elbow bolts. But they can break while tightening which can be frustrating to get cleared out.
The bolts need to match the thread size specified in the OpenSCAD. Most hardware stores will carry these bolts.

Sheet metal screws (#4 pan head) of appropriate length for attaching socket wrist to Palm (1 ea.) and for attaching LatchCover to Upper Arm (1 ea.) The #4 size is US standard, outside the US it is a 3mm sheet metal screw.

ThreadLocker Blue Gel
Once you have assembled everything, it is recommended to put on the bolt threads so they do not work loose. You can use glue if you do not have this.

Rivets and/or Chicago screw/post Applicable to the leather option only. For smaller sizes, we prefer copper rivets. They are small and can be cut to length. The down side is you can crush the plastic if you are not careful. https://www.amazon.com/gp/product/B08HMYMFWS
For larger sizes we prefer Chicago screws. They are reusable, but only come in a limited number of lengths and diameters.
Make sure the correct diameter of the shaft is set in the OpenSCAD options

Leather We recommend ~4.5 oz leather (~1.8mm thick). It is the more expensive option compared to plastic, but we believe it to be more comfortable than the plastic. You can print the leather template SVG file on paper, and use that to determine how much leather you will need.
A leather punch is recommended to make accurate holes in the leather where it will attach to the plastic components. A website of one supplier of cowhide leather is www.montanaleather.com

### To determine which size and length to purchase for the elbow and palm bolts, use the 3-D printed bolts and the parameters on OpenSCAD. It is

helpful to bring the sample 3-D printed bolts with you to the store.

### Both metal and nylon bolts can be cut if they are too long and if you have the

proper tools.

## Identify and Arrange Parts

## Identify the correct parts for the fingers and palm and

arrange them in order.

## The finger pieces have

numbers embossed in them.

## These correspond to the finger numbers 1 to 5 starting

with the thumb.

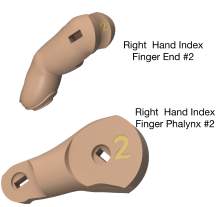
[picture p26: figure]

## The location of the number on the fingers will verify that you

have a Right or Left Hand.

## Prepare the Printed Parts

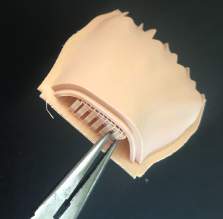
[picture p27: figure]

# Thoroughly Remove the Scaffolding

## This is an important step. Make sure you remove all scaffolding in

the corners and edges.

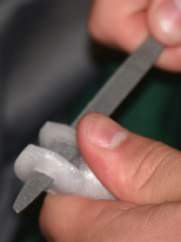
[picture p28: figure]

# Sand, File and Smooth Parts

## Sand, file and generally finish the parts. If you oriented the finger phalanx as suggested during the printing process, you will need to sand the curved back end of the parts. The added supports and spreading will mean the back is not

round.

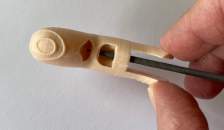
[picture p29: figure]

## Clean string channels

## In smaller printed hands the holes for the strings can close during the printing process. Galvanized picture wire is generally stiff enough to force through the holes to open

them up.

## You can also force the wire through the opening, heat it with a solder iron, and move it around to smooth

the inside of the channels.

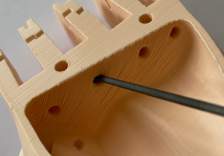
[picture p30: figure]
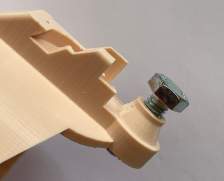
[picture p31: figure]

## Clean the Palm and Elbow threads Using a metal bolt or a tap tool,try screwing the bolts into just the threaded part. The top of the palmtop and the elbow have threads matching what was set by

OpenSCAD.

## You may need to heat the bolt to

help clean the plastic threads.

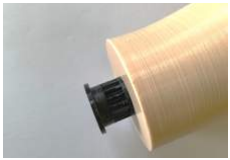
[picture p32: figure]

## Clean the wrist bolt threads Try screwing the wrist bolt in the forearm. Make sure it is smooth and

easy to tighten all the way.

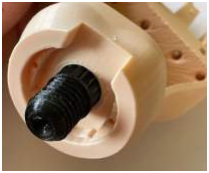
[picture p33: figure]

## Clean wrist button mechanism The wrist button is printed with very tight tolerances. You will likely need to sand the ratcheting part of the

wrist bolt to a smooth round finish.

## Insert the wrist bolt from the inside of the palm. Make sure it rotates easily, yet is sung

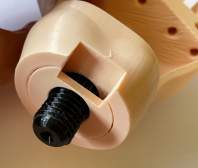
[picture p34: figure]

## Put the Wrist cover over the wrist bolt, WITHOUT the WRIST BUTTON. Make sure the wrist bolt can rotate smoothly and easily yet

does not rattle.

## Take the wrist bolt back out after

the test.

B. Hand Assembly
1. Gather all parts of the hand together. Each finger end and phalanx has a number that is imprinted on it, i.e. 1=thumb, 2=index, 3=middle, 4=ring, and 5=pinky. Fit the pieces together —all should fit and move without undo friction that might impede bending. It may be necessary to use a file, utility knife, or sandpaper to facilitate finger movement. The rectangular holes should also be free of burrs or print filament webbing.
2. Insert the TPU hinges in the slots between the finger ends and the finger phalanxes. Insert other TPU hinges in the phalanx top and slide the ends into the slots in the Palm.
3. Stringing the hand is fairly straightforward and much easier than previous Kwawu versions. Figure 1 shows the fingers and the stringing route. Figure 1 along with Figure 2 shows a hand strung appropriately.
4. There is a structure at the end of each finger for tying a knot. Use Super glue to fix the knots from slipping. Note that the long end of the secondary whippletree is toward the thumb and String 1 from the thumb connects to it (Figure 2). String 2 connects index finger end to middle finger end via the thumb end of the primary whippletree. Note the imprinted arrow on the primary whippletree will point toward the thumb. String 3 connects the ring finger end to pinky finger end via the end opposite the thumb end of primary whippletree.
5. Figure 2 shows shows how the whippletrees are connected to the fingers (Strings 1,2, and 3) and the whippletrees to each other (String 4). String 5 connects to the center hole in the Secondary Whippletree and extends to the Tensioner (Tensioner not shown). String 5 needs to be long enough to reach from the secondary whippletree to the bicep areas of the recipient’s arm. It is
recommended to attach String 5 later in the assembly process (see Step 7 in Forearm Assembly).

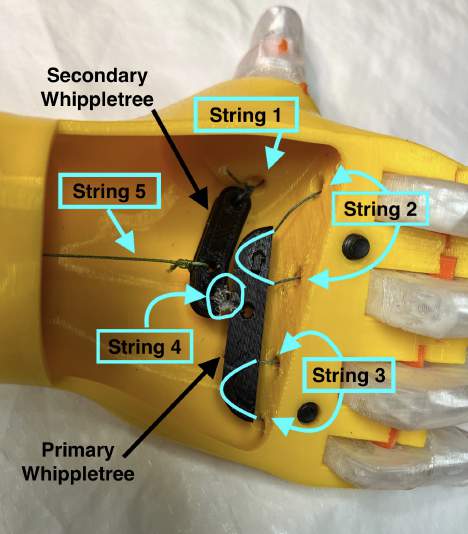
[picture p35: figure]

6.

### Figure 2: Stringing the hand: Palm

7. As shown in Figure 2, with all fingers extended, the the Primary Whippletree should be close to the area in the palm where Strings 2 and 3 enter the palm area. When the Whippletrees are tied together (String 4) and thumb extended, the thumb side of secondary whippletree should be close to the palm area where String 1 enters the palm. This will give the whippletrees adequate room to move when fingers and thumb are clenched.
8. Figure 3 shows components in the wrist. To make sure parts will function properly when assembled, first make sure that the WristButton and WristCover will fit over the WristBolt all the way to the WristBolt pedestal and are able to turn freely. The WristCover was designed to be a tight fit, so it may be necessary to grind/file the ID of the WristCover so that it will fit and turn properly. Also the WristBolt must fit into the hole on the palm top and be able to turn freely. Again, the ID of the Palm top hole may have to be expanded by filing/grinding.

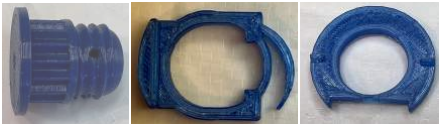
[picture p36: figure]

Figure 3 : Wrist Components
9. Test the WristBolt to make sure it threads into the ForearmArm. Filing in the threads of the bolt may be required to initially get the WristBolt fully engage in the Forearm threads. The application of a dry lubricant to the threads will help to obtain smooth turning of the bolt into the forearm. After obtaining smooth threading of the bolt into the socket, remove the WristBolt from the forearm.
10. Place the WristButton into the top of Palm cavity. While pushing the button, insert the WristBolt into Palm cavity and push the threads out of the top opening. Then place the WristCover over WristButton such that the wedge shaped structures fit with the recesses in the Palm top.

## C. Forearm Assembly

1. If the forearm was printed in two parts, glue the UpperArm and LowerArm together with two part epoxy.
2. Prepare to assemble the latch mechanism—Latch, LatchCover, Ratchet, and Tensioner onto the UpperArm. See Figure 4.

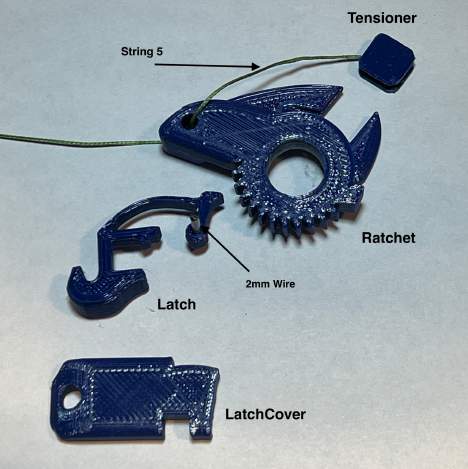
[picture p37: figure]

Figure 4: Latch Mechanism

3. Cut a piece of 2mm wire/hanger to span from the hole in the UpperArm Latch recess, through the Latch and into the hole in the LatchCover. The hole in the Latch may have to be widened to be able to insert the wire—use appropriate sized drill bit if necessary. Insert the wire in the Latch hole to act as an axel in the Latch and set the Latch with wire into the forearm recess.

4. Place the LatchCover over the Latch making sure the wire is inserted in the hole supplied. Use a #4 pan head sheet metal screw to attach the LatchCover to the Forearm.
5. With the Latch pulled back (off position), place the Ratchet in place. Make sure the Latch will engage in the Ratchet teeth when in the forward (on) position.
6. Insert the Tensioner in the slot in the side of the Ratchet (see Figure 4). It should fit in all four of the possible orientations. Some trimming of the Tensioner may be required in certain orientations.
7. Push one end of String 5 through the Egress Port in the side of the forearm and down through the threaded region. See Figure 5. With the hand still disconnected from the forearm, continue pushing the string through the hole in the WristBolt and into the Palm cavity. Attach the string to the center hole of the Secondary Whippletree as shown in Figure 2.
8. Screw the WristBolt on the Forearm until tight, then back off until you see (through the ForearmWrist Lock hole) the first of the 4 holes that is in the WristBolt. Use a sheet metal screw to secure the Wristbolt to the Forearm. (See Figure 5)

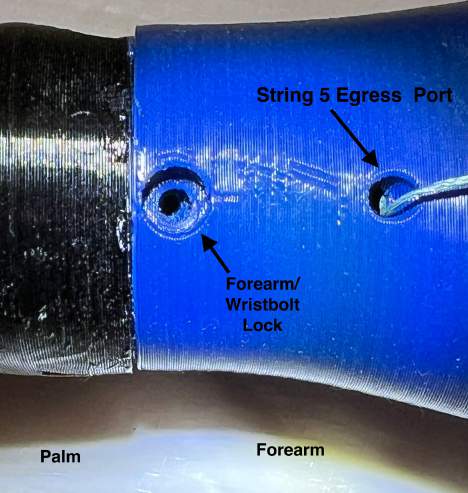
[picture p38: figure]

Figure 5: Forearm to Palm
9. Cut String 5 such that it extends past the Ratchet on the forearm. Thread the free end of the string up through the hole in the Ratchet as shown in Figure 4, then tie it to the to the Tensioner through the center hole in it’s axel. Super glue the both knots in String 5. The PalmCover can now be attached over the palm cavity by fastening it with 2 bolts selected earlier.

## D. Cuff Assembly

1. Plastic Cuff: The Plastic Cuff is ready to connect with the Forearm as printed
2. Leather Cuff:
a. Lay the leather (cut previously) flat with the top smooth surface that will eventually be in the contact with the skin of the recipient. Place the printed Cuff1 under the left side of the leather and Cuff2 under the right side. Verify the holes in the cuffs line up with the holes in the leather.
b. Attach the leather to the Cuff1 and Cuff2 printed parts using Rivets or Chicago type fasteners. Push the fasteners through the leather and plastic and seal from the plastic side.
3. Both Plastic and Leather Cuffs
a. Using bolts previously selected, attach Cuff1 to the Ratchet/Latch side of the forearm and attach Cuff2 to the opposite side. It may be helpful to use appropriate size taps to clean out the printed threads.
b. Flex the Cuff and verify finger movement. If String 5 is not tight enough, remove the Tensioner from the Ratchet slot and wind the string tighter and place it back in the Ratchet slot.
4. Velcro Strap Install
a. Use a strap having the width as chosen initially and thread it through the gaps between the plastic or leather and through the attached loop at the velcro end. The strap will allow the cuff to be tightened as necessary

## E. Padding Install

1. Plastic Cuff:
a. Silicone Option: Cut the silicone in a pattern to fit inside the plastic grid on the cuff. Glue the silicone to the grid with a flexible adhesive.
b. Neoprene Option: Cut the self adhesive neoprene to fit inside the plastic grid on the Cuff. Peal the backing and stick it onto the grid.
2. Leather Cuff—the leather Cuff does not need padding
3. Socket
a. The padding needs to be just long enough to cover the recipient’s residual but shorter as to not cover any existing vent holes. Make a paper template of the inside of the socket and use it as a pattern for silicone or neoprene padding.
b. Silicone Option: Cut the silicone to the pattern and dry fit it inside. the socket-some trimming may be required. Glue the silicone to the inside to the socket with a suitable adhesive.
c. Neoprene Option: Cut the neoprene to the pattern and dry fit it inside the socket-some trimming may be required. Remove the backing paper and self adhere the neoprene inside the socket.

## F. Final Comments

1. Plasti Dip is commonly used on fingers and palms to enhance the ability of the Kwawu 3 to pick and hold things because it adds tackiness to the plastic fingers. Plasti Dip Primer is recommended prior to painting with the Plasti Dip. The joints and strings in the fingers should not be exposed to Plasti Dip.
2. Lee Tippy nail’s Gel Finger Tips can be purchased and placed over the ends of the plastic fingers to enhance gripability.

## Final Testing

1. Exercise the wrist lock mechanism to make sure the hand can be turned 360 degrees and can be locked at any selected location.
2. Exercise the latch mechanism. In the engaged position, the latch should lock the fingers in position depending on the extent of elbow rotation.
3. With the latch in the engaged position, fingers should maintain their clutched position even when the elbow is straightened,

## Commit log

2022-04-11 initial Release
    [Kwawu 3.0- Socket.scad, o_Arm1.stl, o_Arm2.stl, o_Cuff1.stl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]
2025-05-20 Working better with newer OpenSCAD versions
    [Kwawu 3.0- Socket.scad]

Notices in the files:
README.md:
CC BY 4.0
